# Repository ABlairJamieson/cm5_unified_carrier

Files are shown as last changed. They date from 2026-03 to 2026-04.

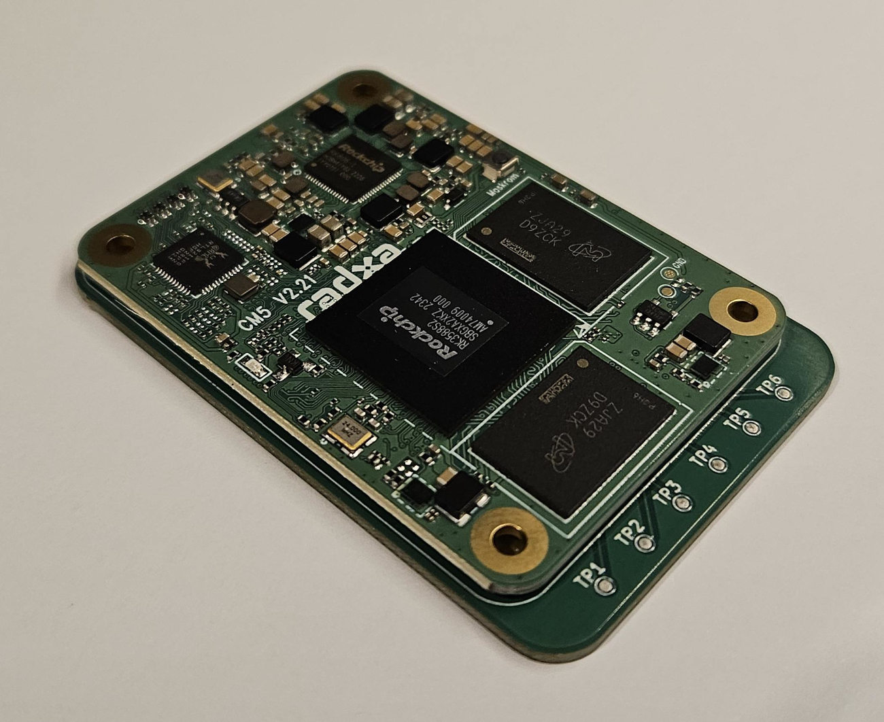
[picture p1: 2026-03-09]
include/radxa-cm5-kicad-main/radxa-cm5-kicad-main/screenshots/pcb-photo.jpg

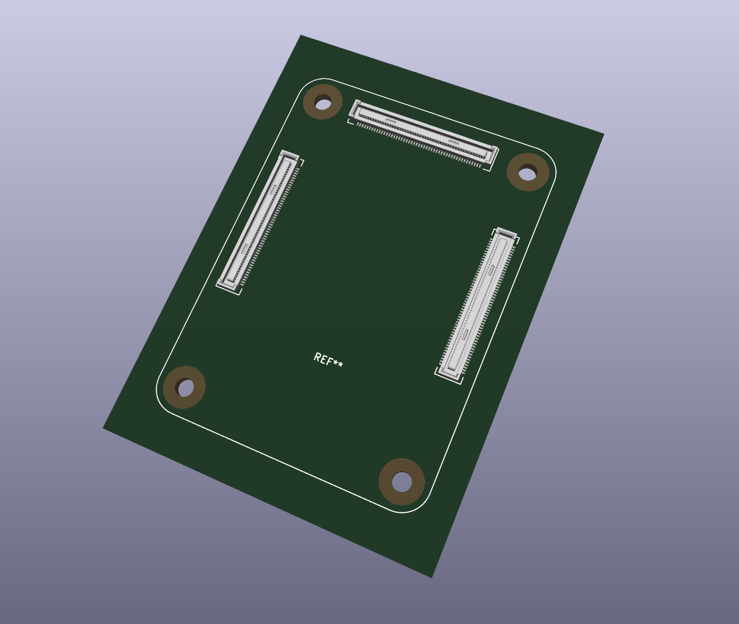
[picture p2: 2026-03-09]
include/radxa-cm5-kicad-main/radxa-cm5-kicad-main/screenshots/3d-model.png

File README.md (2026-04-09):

# CM5 Unified Carrier

Carrier board for Radxa CM5 used in the Hyper-K camera system.

Features:
- 48V input
- PoE option
- USB3 camera interface
- Ethernet
- Uses drop in DC/DC modules for 48V->12V (ext power mode)
- Uses drop in DC/DC module for 12V->8V (IWCD camera)
- Uses drop in DC/DC module for 12V->5V (both cameras)



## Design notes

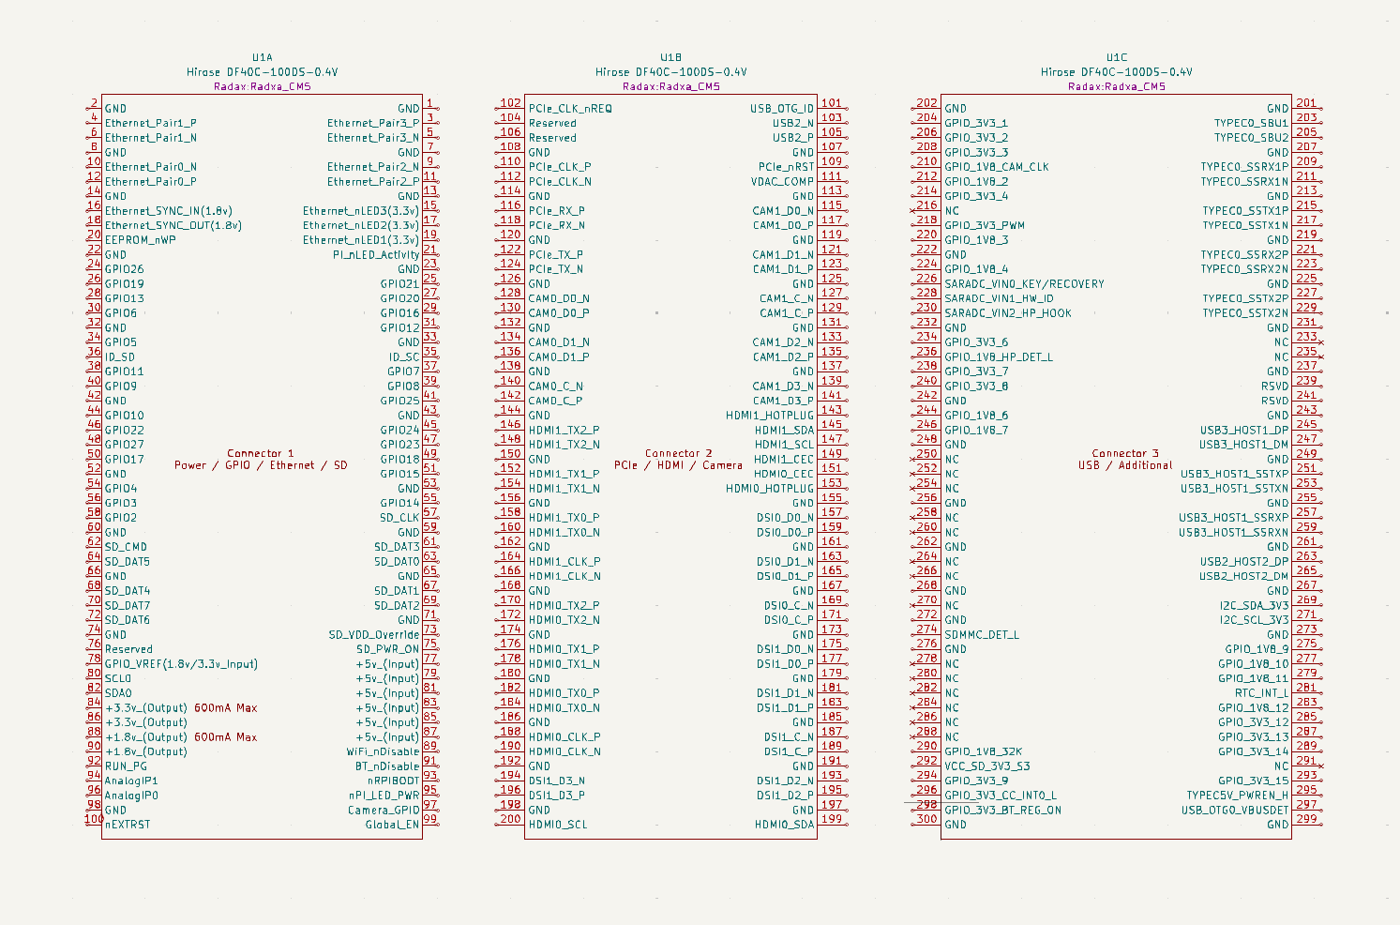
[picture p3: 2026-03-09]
include/radxa-cm5-kicad-main/radxa-cm5-kicad-main/screenshots/schematic.png

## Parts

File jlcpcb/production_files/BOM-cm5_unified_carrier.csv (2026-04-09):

Comment | Designator | Footprint | LCSC | Quantity
0Ohm | R101,R102 | R_1206_3216Metric_Pad1.30x1.75mm_HandSolder | C17888 | 2
10uF | C101,C102,C103,C406 | C_1206_3216Metric_Pad1.33x1.80mm_HandSolder | C89632 | 4
1uF | C302 | C_0805_2012Metric_Pad1.18x1.45mm_HandSolder | C28323 | 1
22uF | C404 | C_1206_3216Metric_Pad1.33x1.80mm_HandSolder | C12891 | 1
484050003 | J103 | CONN_484050003_MOL | C6058327 | 1
SMAJ58A | D101,D201 | D_SMA | C151246 | 2
PJ-102AH | J102 | CUI_PJ-102AH |  | 1
7499511002A | J201 | T_Wurth_WE-RJ45LAN_7499511002A |  | 1
436500403 | J101 | MOLEX_436500403 |  | 1
AG5712-LPB | U201 | MODULE_AG5712-LPB |  | 1
GND | TP403 | TestPoint_Pad_D1.5mm |  | 1
V8 | TP401 | TestPoint_Pad_D1.5mm |  | 1
GND | TP302 | TestPoint_Pad_D1.5mm |  | 1
V12 | TP301 | TestPoint_Pad_D1.5mm |  | 1
1.34kOhm | R402 | R_0805_2012Metric_Pad1.20x1.40mm_HandSolder |  | 1
2.49kOhm | R401 | R_0805_2012Metric_Pad1.20x1.40mm_HandSolder |  | 1
DNP | R301 | R_0805_2012Metric_Pad1.20x1.40mm_HandSolder |  | 1
I6A24014A033V-002-R | PS401 | CONV_I6A24014A033V-002-R |  | 1
ULS-12_5-D48N-C | PS301 | CONV_ULS-12_5-D48N-C |  | 1
OKL2-T_6-W12N-C | MD401 | MURATA_OKL2-T-6-W12N-C_0 |  | 1
PJ-102AH | J401 | CUI_PJ-102AH |  | 1
FerriteBead | FB101 | FB_Wurth_WE-CBF-1206_W5.2 |  | 1
10uF | C405 | C_1206_3216Metric_Pad1.33x1.80mm_HandSolder |  | 1
22uF | C403 | C_1206_3216Metric_Pad1.33x1.80mm_HandSolder |  | 1
0.1 uF | C402 | C_0805_2012Metric_Pad1.18x1.45mm_HandSolder |  | 1
100 uF | C401 | CP_Elec_6.3x5.8 |  | 1
10uF | C301 | CP_Elec_6.3x5.4 |  | 1
470uF | C204 | CP_Elec_8x6.5 |  | 1
10uF | C203 | C_1206_3216Metric_Pad1.33x1.80mm_HandSolder |  | 1
1uF | C202 | C_0805_2012Metric_Pad1.18x1.45mm_HandSolder |  | 1
10nF | C201 | C_1206_3216Metric_Pad1.33x1.80mm_HandSolder |  | 1
Hirose DF40C-100DS-0.4V | J501 | Radxa_CM5 |  | 1
484050003 | J104 | CONN_484050003_MOL |  | 1
1050170001 | J105 | USB_Micro_B_Female_1050170001 |  | 1
Conn_01x02_Pin | J601 | PinHeader_1x02_P2.54mm_Vertical |  | 1
SW_Push | SW501 | SW_SPST_EVQP7A |  | 1
V5 | TP402 | TestPoint_Pad_D1.5mm |  | 1
PoE+ | TP202 | TestPoint_Pad_D1.5mm |  | 1
PoE- | TP201 | TestPoint_Pad_D1.5mm |  | 1
ABS10 | BR201 | SOT200P640X160-4N |  | 1
ABS10 | BR202 | SOT200P640X160-4N |  | 1

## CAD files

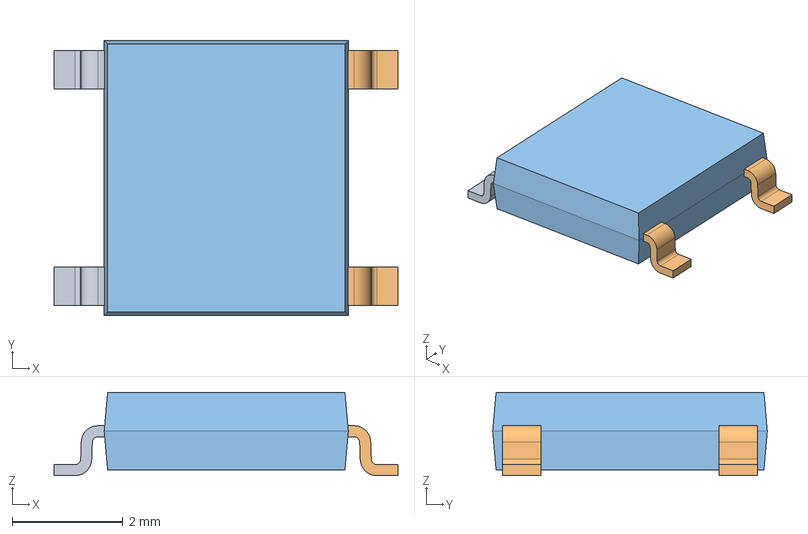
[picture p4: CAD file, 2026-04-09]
include/ABS10/ABS10.step
6.20 x 4.95 x 1.50 mm

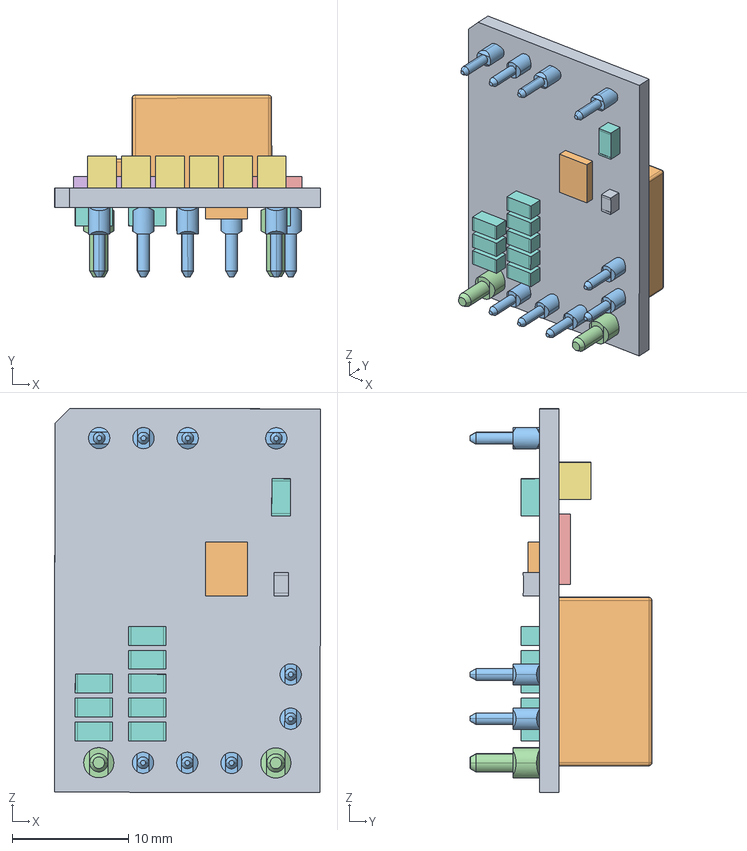
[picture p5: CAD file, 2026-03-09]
include/I6A24014A033V-002-R/I6A24014A033V-002-R.step
22.9 x 15.7 x 33.0 mm
I6A_PCB
I6A_OUTPUT_INDUCTOR
ZP00166_01- x 9
ZP00167_01- x 2
I6A_LOW_SIDE_FET
I6A_HIGH_SIDE_FET x 2
1210_CAP_COLOR x 6
1206_CAP_COLOR x 9
0805_CAP
I6A_CONTROL_IC2

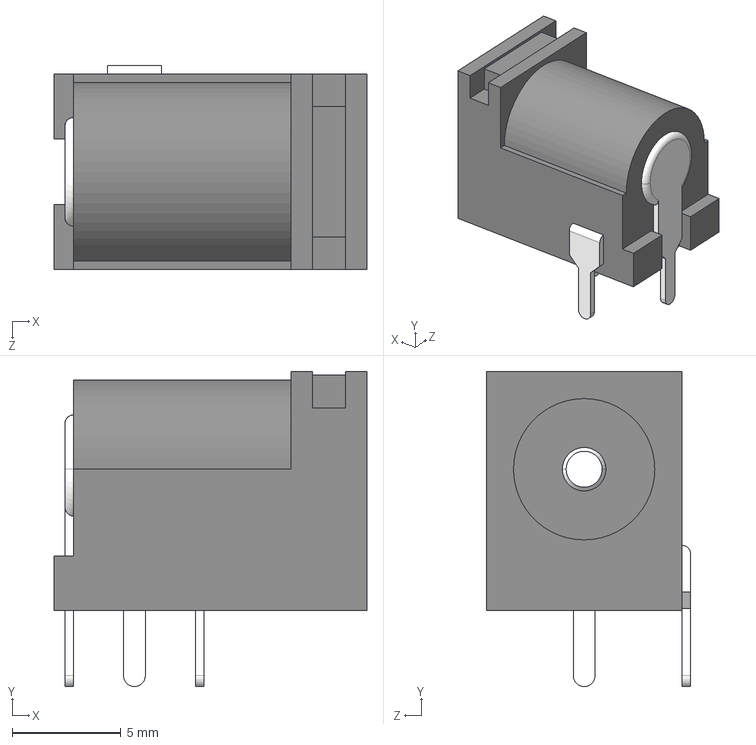
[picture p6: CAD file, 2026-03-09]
include/PJ-102AH/PJ-102AH.step
14.4 x 14.5 x 9.40 mm

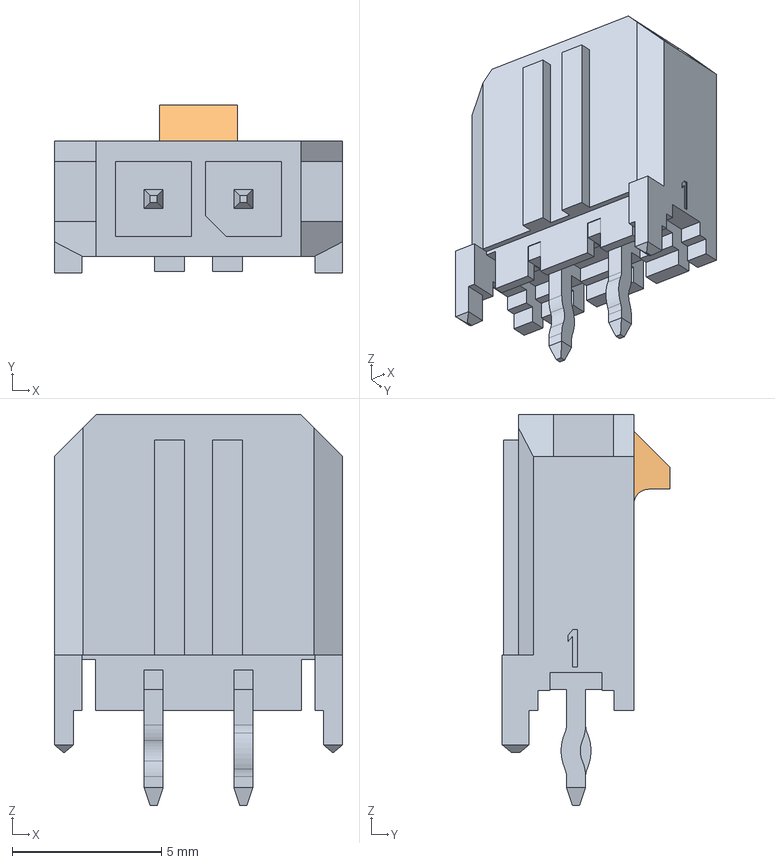
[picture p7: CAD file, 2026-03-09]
include/436500215/436500215.step
9.65 x 5.61 x 13.1 mm

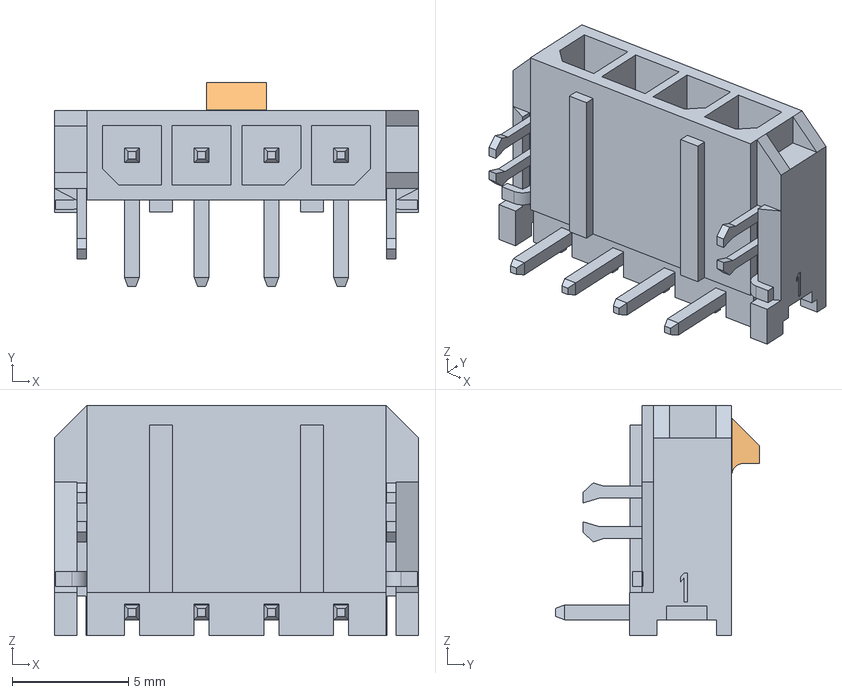
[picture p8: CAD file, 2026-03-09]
include/436500403/436500403.step
15.7 x 8.79 x 9.90 mm

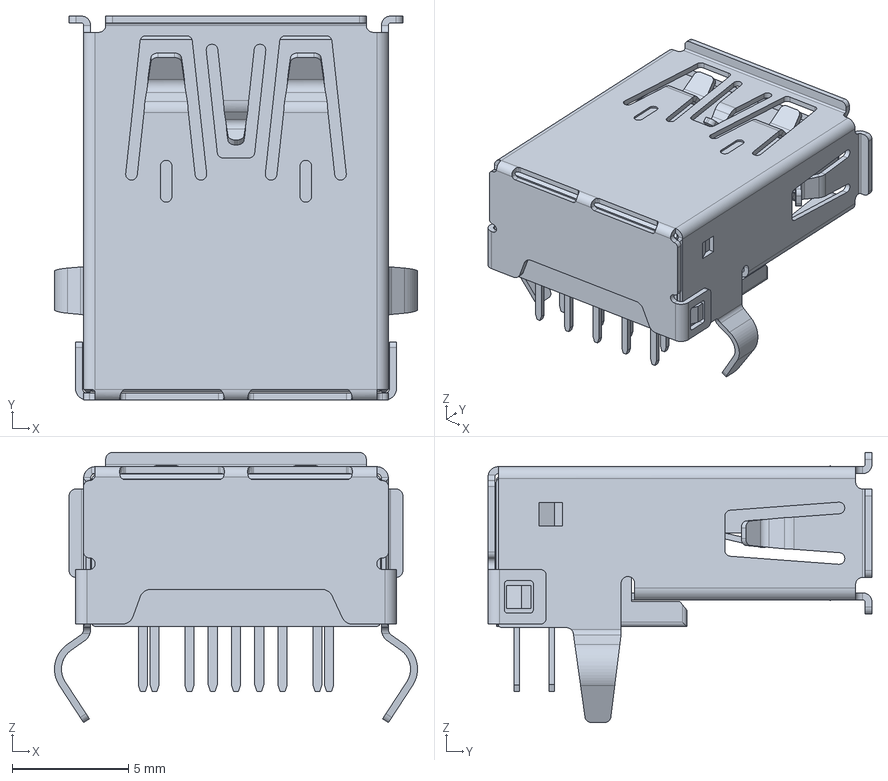
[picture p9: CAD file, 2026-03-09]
include/484050003/484050003.stp
15.6 x 16.5 x 11.6 mm

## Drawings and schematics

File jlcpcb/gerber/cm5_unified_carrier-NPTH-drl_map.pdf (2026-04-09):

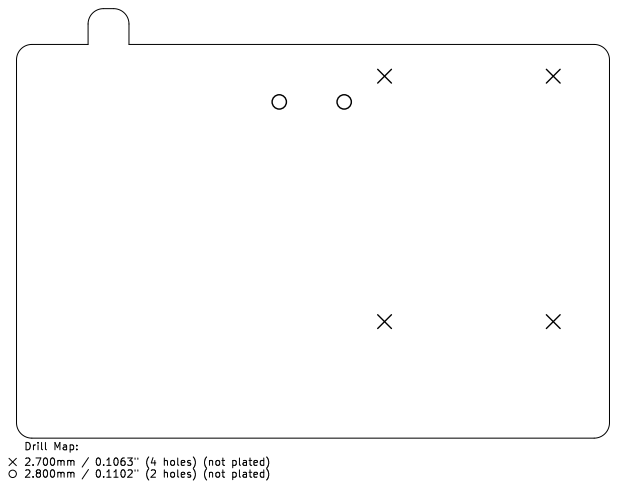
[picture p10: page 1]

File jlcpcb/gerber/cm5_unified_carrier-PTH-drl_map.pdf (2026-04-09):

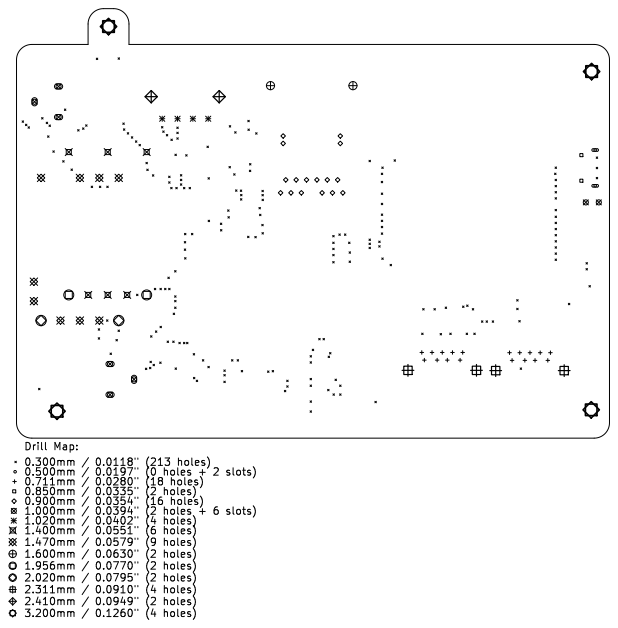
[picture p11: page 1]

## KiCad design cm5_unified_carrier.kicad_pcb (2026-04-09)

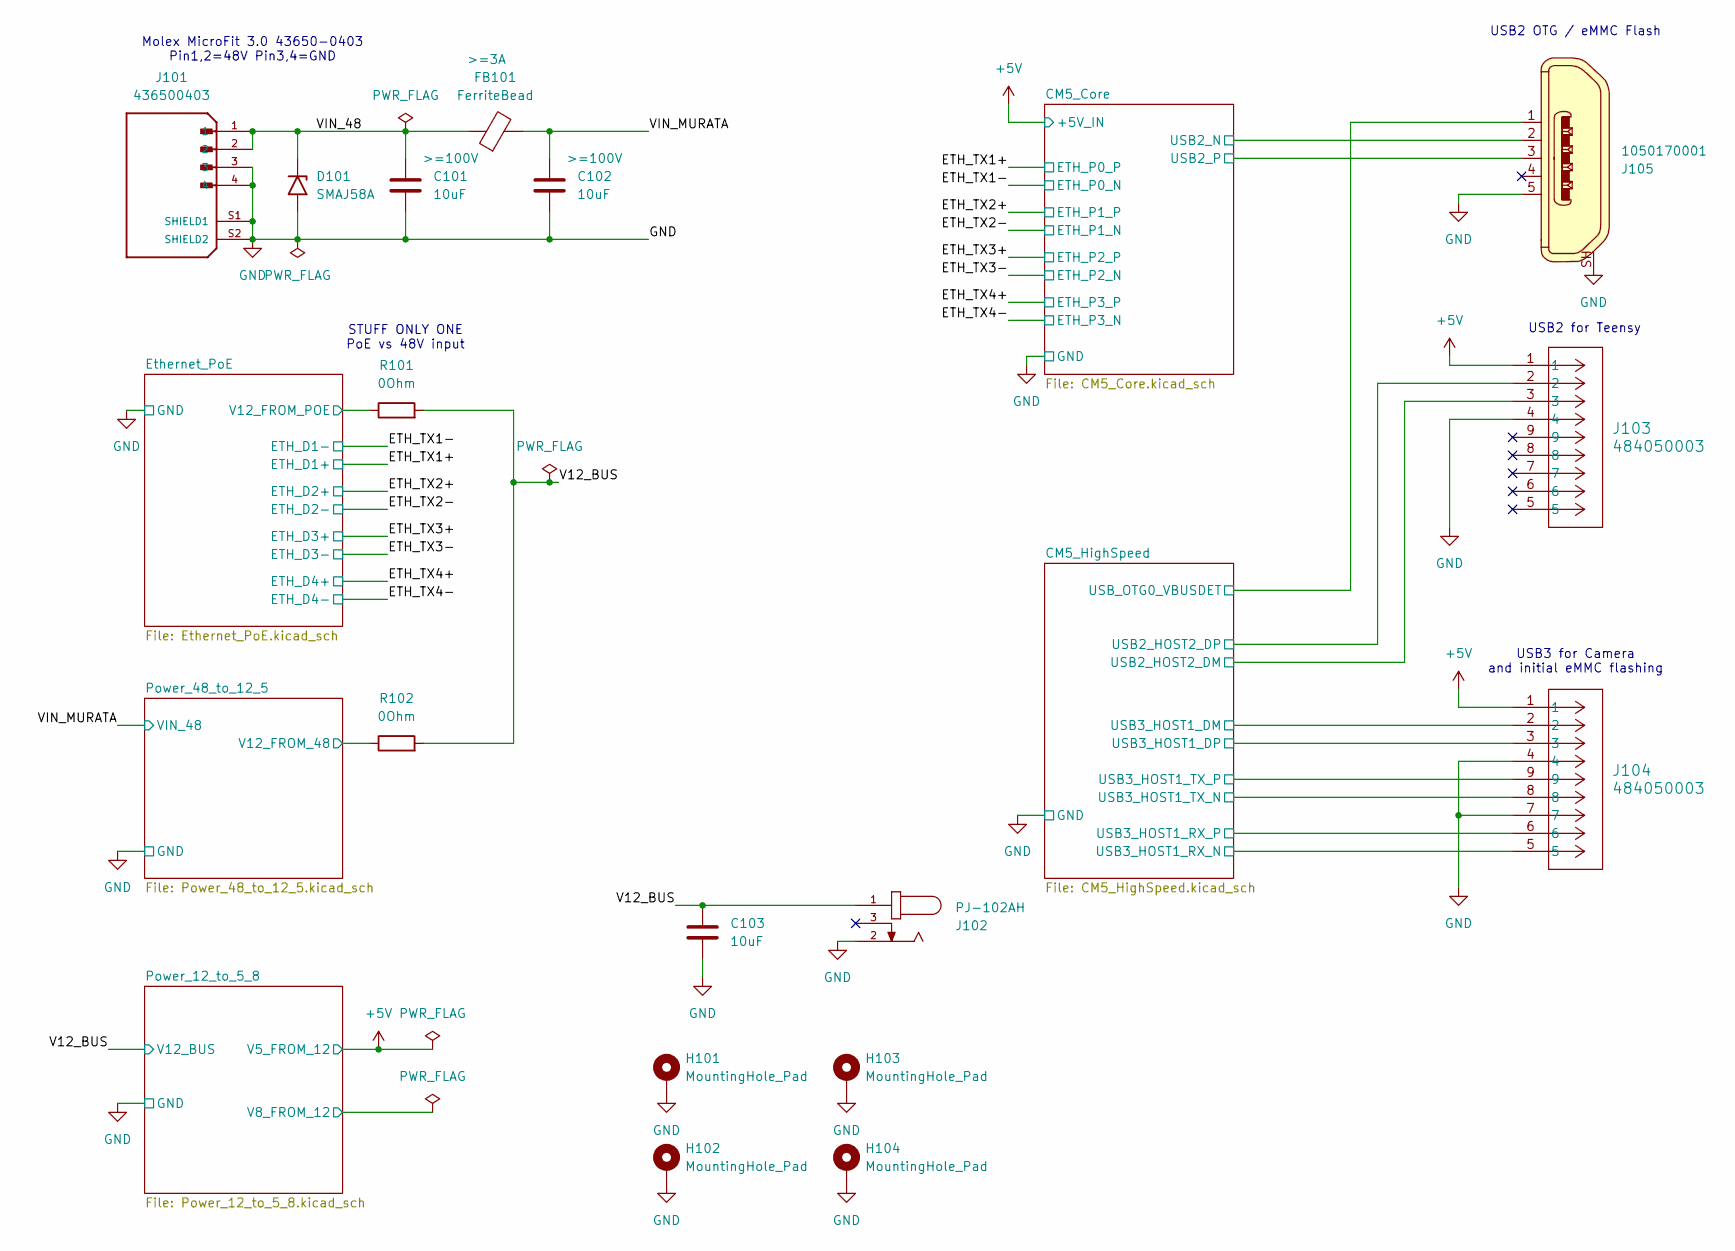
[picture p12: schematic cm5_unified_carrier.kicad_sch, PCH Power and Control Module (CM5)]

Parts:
C101, C102, C103: 10uF; C_1206_3216Metric_Pad1.33x1.80mm_HandSolder
D101: SMAJ58A; D_SMA
FB101: FerriteBead; FB_Wurth_WE-CBF-1206_W5.2
H101, H102, H103, H104: MountingHole_Pad; MountingHole_3.2mm_M3_DIN965_Pad
J101: 436500403; MOLEX_436500403; PARTREV F3
J102: PJ-102AH; CUI_PJ-102AH
J103, J104: 484050003; CONN_484050003_MOL
J105: 1050170001; USB_Micro_B_Female_1050170001; MPN 1050170001; Digi-Key_PN WM1399CT-ND
R101, R102: 0Ohm; R_1206_3216Metric_Pad1.30x1.75mm_HandSolder

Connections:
+5V: J103.1, J104.1; also elsewhere on the board
/CM5_Core/USB2_N: J105.2; also elsewhere on the board
/CM5_Core/USB2_P: J105.3; also elsewhere on the board
/CM5_HighSpeed/USB2_HOST2_DM: J103.3; also elsewhere on the board
/CM5_HighSpeed/USB2_HOST2_DP: J103.2; also elsewhere on the board
/CM5_HighSpeed/USB3_HOST1_DM: J104.2; also elsewhere on the board
/CM5_HighSpeed/USB3_HOST1_DP: J104.3; also elsewhere on the board
/CM5_HighSpeed/USB3_HOST1_SSRXN: J104.5; also elsewhere on the board
/CM5_HighSpeed/USB3_HOST1_SSRXP: J104.6; also elsewhere on the board
/CM5_HighSpeed/USB3_HOST1_SSTXN: J104.8; also elsewhere on the board
/CM5_HighSpeed/USB3_HOST1_SSTXP: J104.9; also elsewhere on the board
/CM5_HighSpeed/USB_OTG0_VBUSDET: J105.1; also elsewhere on the board
/Ethernet_PoE/V12_FROM_POE: R101.1; also elsewhere on the board
/Power_48_to_12_5/V12_FROM_48: R102.1; also elsewhere on the board
/V12_BUS: C103.1, J102.1, R101.2, R102.2; also elsewhere on the board
/VIN_48: C101.1, D101.1 (A1), FB101.1, J101.1, J101.2
/VIN_MURATA: C102.1, FB101.2; also elsewhere on the board
GND: C101.2, C102.2, C103.2, D101.2 (A2), H101.1, H102.1, H103.1, H104.1, J101.3, J101.4, J101.S1 (SHIELD1), J101.S2 (SHIELD2), J102.2, J103.4, J104.4, J104.7, J105.5, J105.SH; also elsewhere on the board

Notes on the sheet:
STUFF ONLY ONE PoE vs 48V input
USB2 for Teensy
USB2 OTG / eMMC Flash
USB3 for Camera and initial eMMC flashing
Molex MicroFit 3.0 43650-0403 Pin1,2=48V Pin3,4=GND

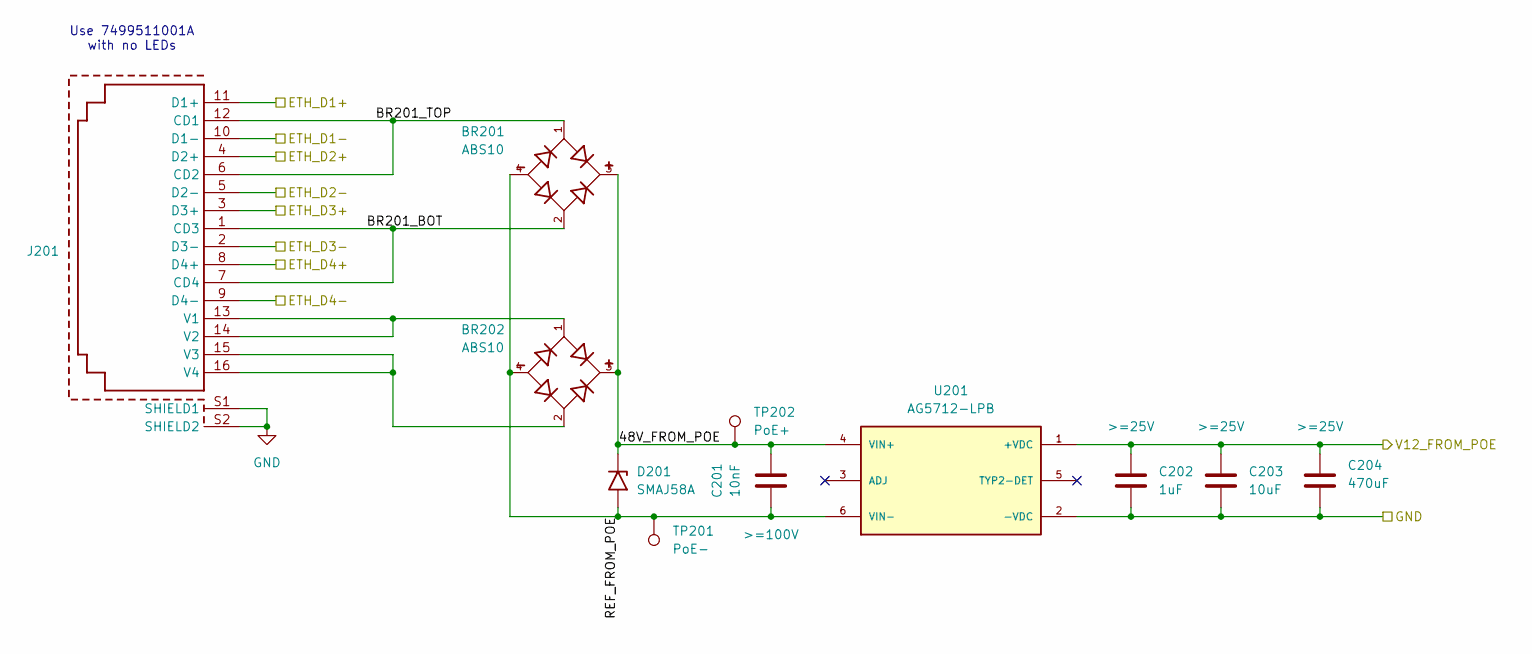
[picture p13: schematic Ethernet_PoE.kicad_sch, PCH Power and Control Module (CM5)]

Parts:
BR201, BR202: ABS10; SOT200P640X160-4N; PART_REV 4
C201: 10nF; C_1206_3216Metric_Pad1.33x1.80mm_HandSolder
C202: 1uF; C_0805_2012Metric_Pad1.18x1.45mm_HandSolder
C203: 10uF; C_1206_3216Metric_Pad1.33x1.80mm_HandSolder
C204: 470uF; CP_Elec_8x6.5
D201: SMAJ58A; D_SMA
J201: 7499511002A; T_Wurth_WE-RJ45LAN_7499511002A; Part Number 7499511002A
TP201: PoE-; TestPoint_Pad_D1.5mm
TP202: PoE+; TestPoint_Pad_D1.5mm
U201: AG5712-LPB; MODULE_AG5712-LPB; PARTREV V1.1

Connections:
/ETH_TX1+: J201.11 (D1+); also elsewhere on the board
/ETH_TX1-: J201.10 (D1-); also elsewhere on the board
/ETH_TX2+: J201.4 (D2+); also elsewhere on the board
/ETH_TX2-: J201.5 (D2-); also elsewhere on the board
/ETH_TX3+: J201.3 (D3+); also elsewhere on the board
/ETH_TX3-: J201.2 (D3-); also elsewhere on the board
/ETH_TX4+: J201.8 (D4+); also elsewhere on the board
/ETH_TX4-: J201.9 (D4-); also elsewhere on the board
/Ethernet_PoE/48V_FROM_POE: BR201.3, BR202.3, C201.2, D201.1 (A1), TP202.1, U201.4 (VIN+)
/Ethernet_PoE/BR201_BOT: BR201.2, J201.1 (CD3), J201.7 (CD4)
/Ethernet_PoE/BR201_TOP: BR201.1, J201.6 (CD2), J201.12 (CD1)
/Ethernet_PoE/REF_FROM_POE: BR201.4, BR202.4, C201.1, D201.2 (A2), TP201.1, U201.6 (VIN-)
/Ethernet_PoE/V12_FROM_POE: C202.1, C203.1, C204.1, U201.1 (+VDC); also elsewhere on the board
GND: C202.2, C203.2, C204.2, J201.S1 (SHIELD1), J201.S2 (SHIELD2), U201.2 (-VDC); also elsewhere on the board
unnamed: BR202.1, J201.13 (V1), J201.14 (V2)
unnamed: BR202.2, J201.15 (V3), J201.16 (V4)

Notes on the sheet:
Use 7499511001A with no LEDs

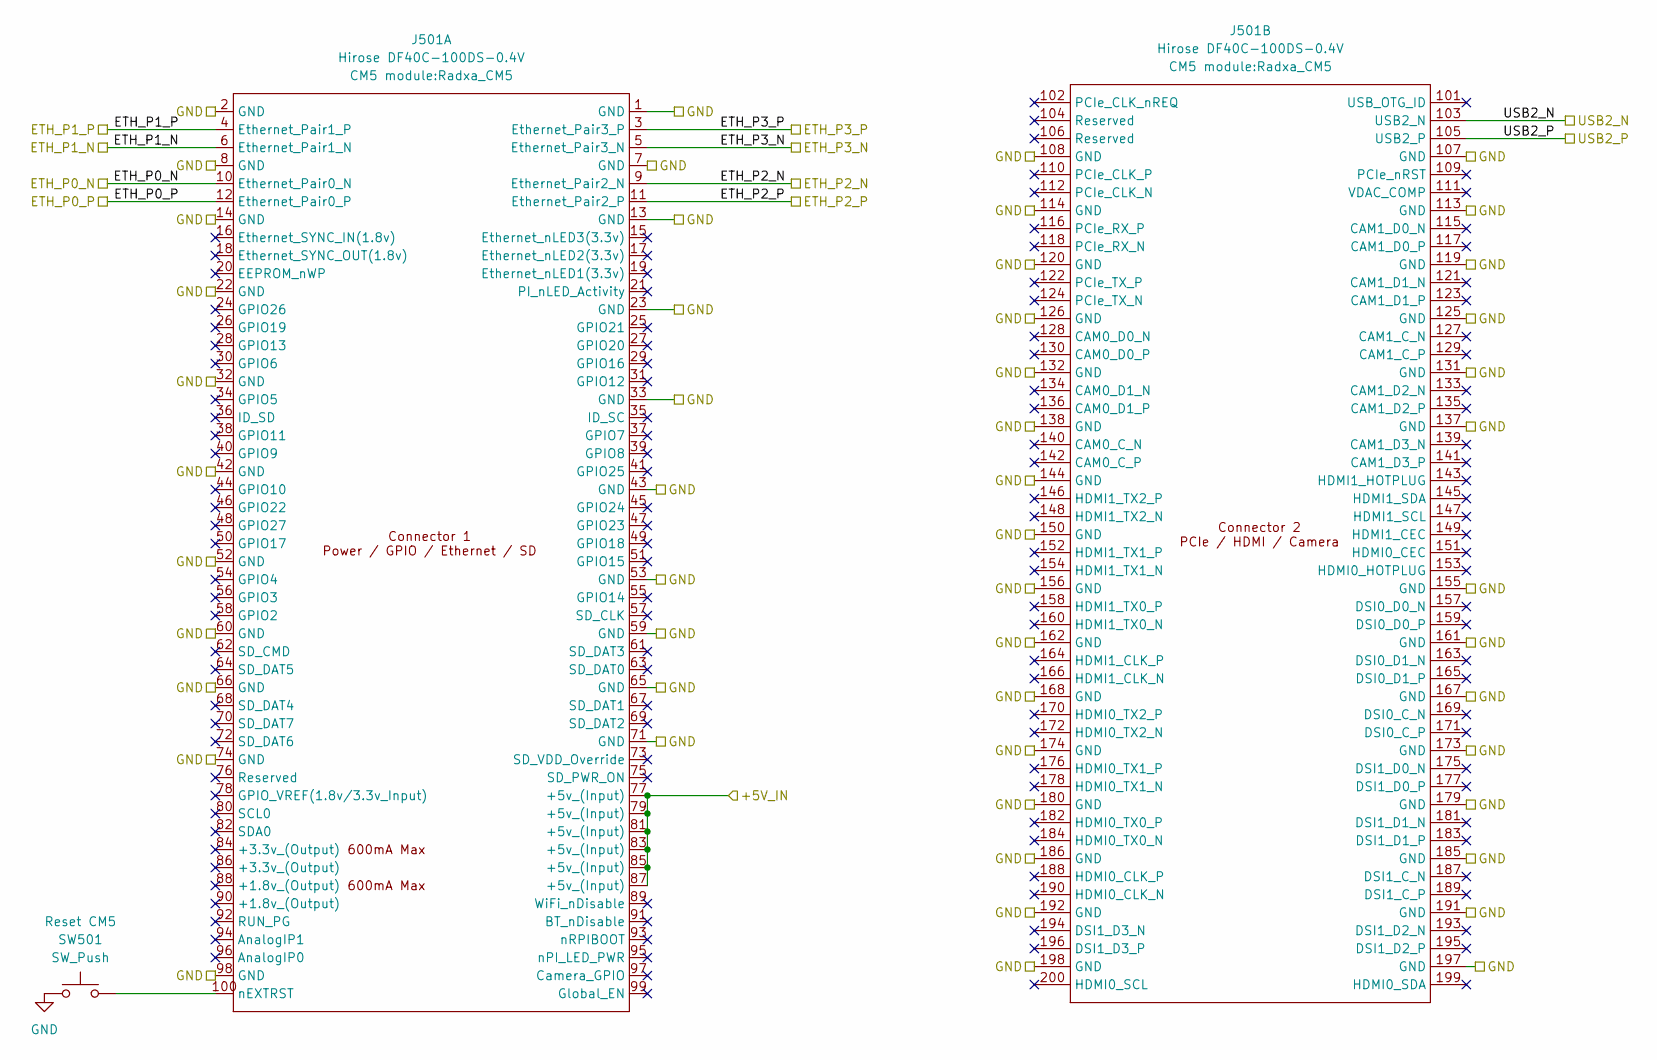
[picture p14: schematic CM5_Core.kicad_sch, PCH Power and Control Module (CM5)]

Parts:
J501: Hirose DF40C-100DS-0.4V; Radxa_CM5
SW501: SW_Push; SW_SPST_EVQP7A

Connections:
+5V: J501.77 (+5v_(Input)), J501.79 (+5v_(Input)), J501.81 (+5v_(Input)), J501.83 (+5v_(Input)), J501.85 (+5v_(Input)), J501.87 (+5v_(Input)); also elsewhere on the board
/CM5_Core/USB2_N: J501.103 (USB2_N); also elsewhere on the board
/CM5_Core/USB2_P: J501.105 (USB2_P); also elsewhere on the board
/ETH_TX1+: J501.12 (Ethernet_Pair0_P); also elsewhere on the board
/ETH_TX1-: J501.10 (Ethernet_Pair0_N); also elsewhere on the board
/ETH_TX2+: J501.4 (Ethernet_Pair1_P); also elsewhere on the board
/ETH_TX2-: J501.6 (Ethernet_Pair1_N); also elsewhere on the board
/ETH_TX3+: J501.11 (Ethernet_Pair2_P); also elsewhere on the board
/ETH_TX3-: J501.9 (Ethernet_Pair2_N); also elsewhere on the board
/ETH_TX4+: J501.3 (Ethernet_Pair3_P); also elsewhere on the board
/ETH_TX4-: J501.5 (Ethernet_Pair3_N); also elsewhere on the board
GND: J501.1 (GND), J501.2 (GND), J501.7 (GND), J501.8 (GND), J501.13 (GND), J501.14 (GND), J501.22 (GND), J501.23 (GND), J501.32 (GND), J501.33 (GND), J501.42 (GND), J501.43 (GND), J501.52 (GND), J501.53 (GND), J501.59 (GND), J501.60 (GND), J501.65 (GND), J501.66 (GND), J501.71 (GND), J501.74 (GND), J501.98 (GND), J501.107 (GND), J501.108 (GND), J501.113 (GND), J501.114 (GND), J501.119 (GND), J501.120 (GND), J501.125 (GND), J501.126 (GND), J501.131 (GND), J501.132 (GND), J501.137 (GND), J501.138 (GND), J501.144 (GND), J501.150 (GND), J501.155 (GND), J501.156 (GND), J501.161 (GND), J501.162 (GND), J501.167 (GND), J501.168 (GND), J501.173 (GND), J501.174 (GND), J501.179 (GND), J501.180 (GND), J501.185 (GND), J501.186 (GND), J501.191 (GND), J501.192 (GND), J501.197 (GND), J501.198 (GND), SW501.1; also elsewhere on the board
unnamed: J501.100 (nEXTRST), SW501.2

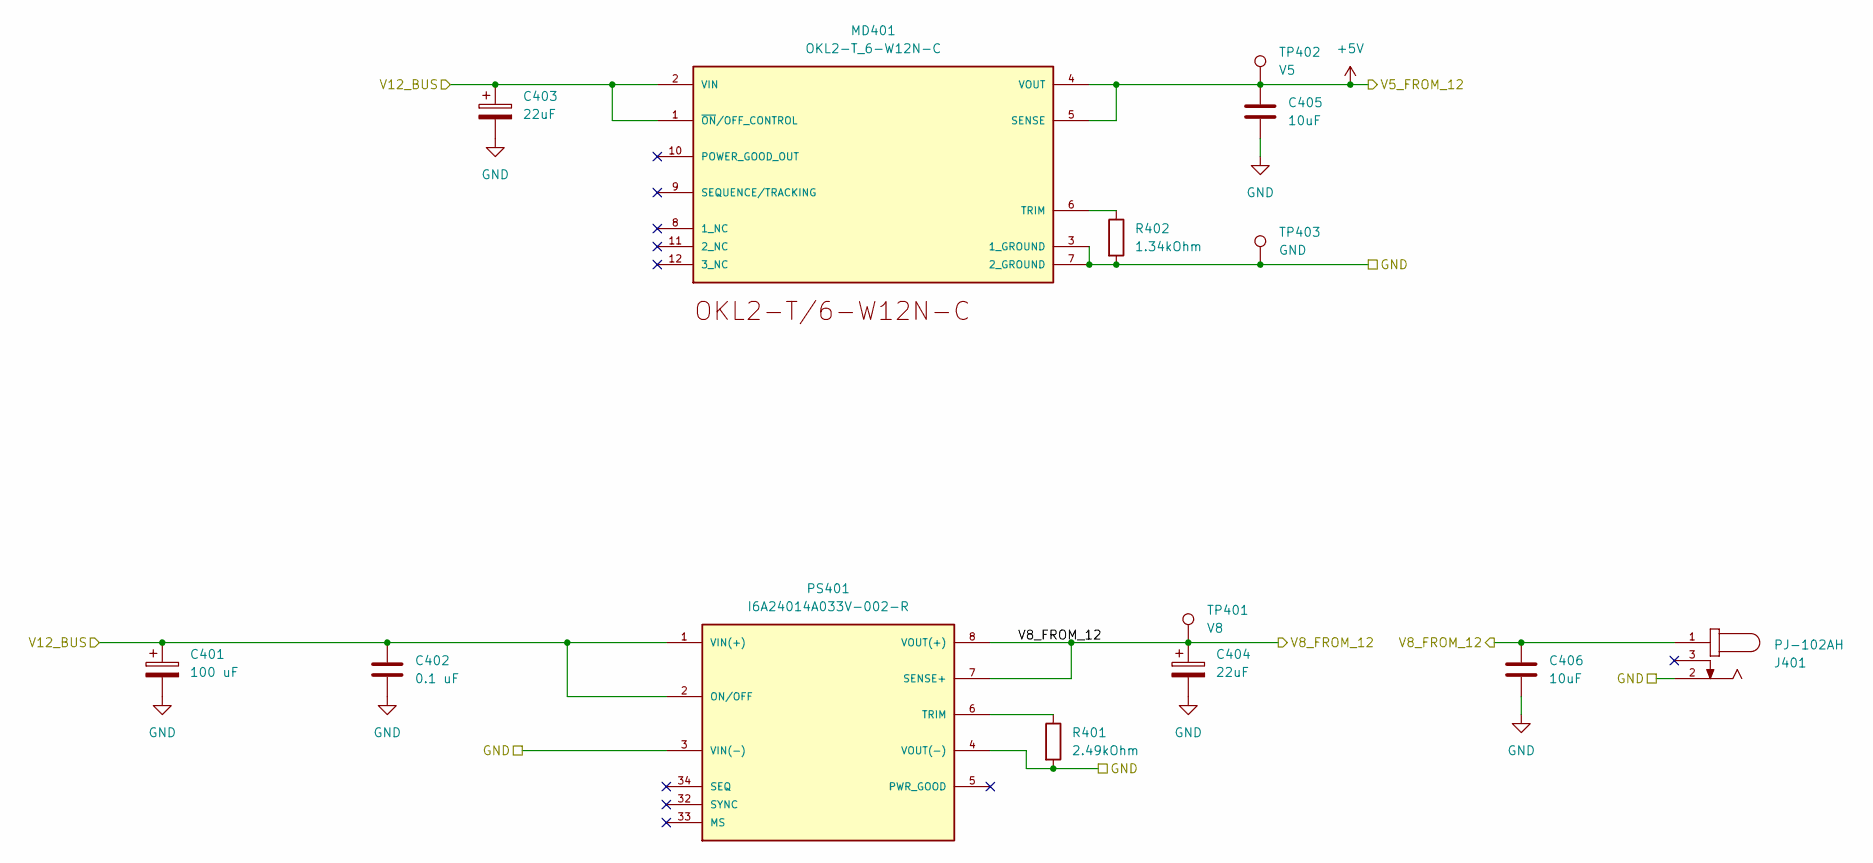
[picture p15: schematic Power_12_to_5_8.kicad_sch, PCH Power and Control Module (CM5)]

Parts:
C401: 100 uF; CP_Elec_6.3x5.8
C402: 0.1 uF; C_0805_2012Metric_Pad1.18x1.45mm_HandSolder
C403, C404: 22uF; C_1206_3216Metric_Pad1.33x1.80mm_HandSolder
C405, C406: 10uF; C_1206_3216Metric_Pad1.33x1.80mm_HandSolder
J401: PJ-102AH; CUI_PJ-102AH
MD401: OKL2-T_6-W12N-C; MURATA_OKL2-T-6-W12N-C_0; MOUSER_PART_NUMBER 580-OKL2-T/6-W12N-C; MOUSER_DESCRIPTION Non-Isolated DC/DC Converters 12Vin .59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
PS401: I6A24014A033V-002-R; CONV_I6A24014A033V-002-R; PARTREV A2; DigiKey_Part_Number 285-2857-ND
R401: 2.49kOhm; R_0805_2012Metric_Pad1.20x1.40mm_HandSolder
R402: 1.34kOhm; R_0805_2012Metric_Pad1.20x1.40mm_HandSolder
TP401: V8; TestPoint_Pad_D1.5mm
TP402: V5; TestPoint_Pad_D1.5mm
TP403: GND; TestPoint_Pad_D1.5mm

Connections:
+5V: C405.1, MD401.4 (VOUT), MD401.5 (SENSE), TP402.1; also elsewhere on the board
/Power_12_to_5_8/V8_FROM_12: C404.1, C406.1, J401.1, PS401.7 (SENSE+), PS401.8 (VOUT(+)), TP401.1
/V12_BUS: C401.1, C402.1, C403.1, MD401.1 (~ON/OFF_CONTROL), MD401.2 (VIN), PS401.1 (VIN(+)), PS401.2 (ON/OFF); also elsewhere on the board
GND: C401.2, C402.2, C403.2, C404.2, C405.2, C406.2, J401.2, MD401.3 (1_GROUND), MD401.7 (2_GROUND), PS401.3 (VIN(-)), PS401.4 (VOUT(-)), R401.2, R402.2, TP403.1; also elsewhere on the board
unnamed: MD401.6 (TRIM), R402.1
unnamed: PS401.6 (TRIM), R401.1

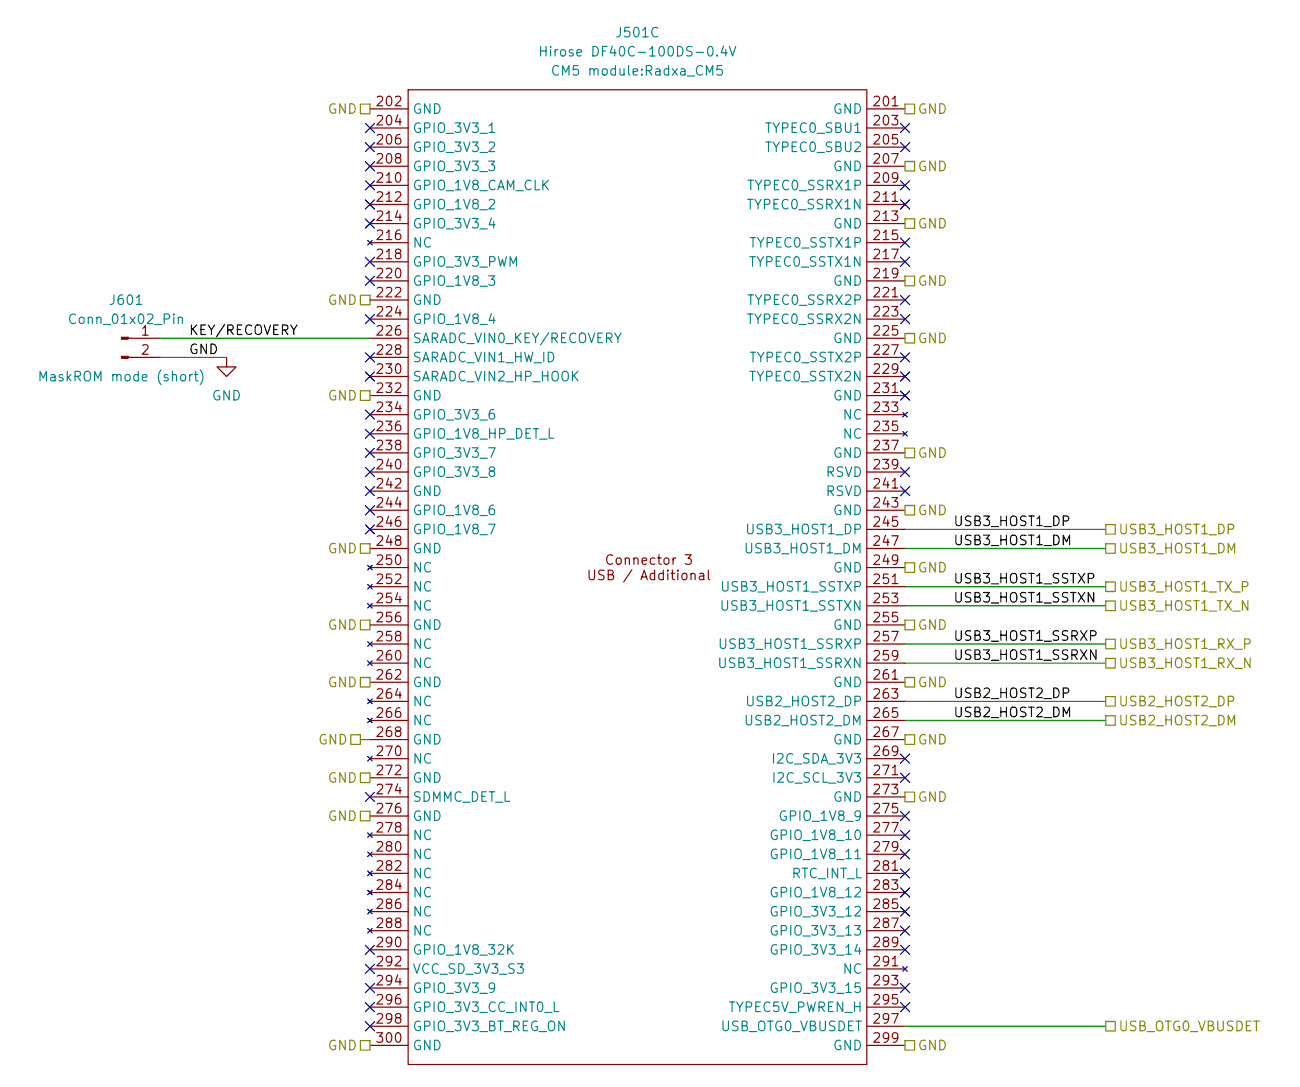
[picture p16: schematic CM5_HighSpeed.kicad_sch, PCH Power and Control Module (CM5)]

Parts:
J501: Hirose DF40C-100DS-0.4V; Radxa_CM5
J601: Conn_01x02_Pin; PinHeader_1x02_P2.54mm_Vertical

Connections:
/CM5_HighSpeed/KEY/RECOVERY: J501.226 (SARADC_VIN0_KEY/RECOVERY), J601.1
/CM5_HighSpeed/USB2_HOST2_DM: J501.265 (USB2_HOST2_DM); also elsewhere on the board
/CM5_HighSpeed/USB2_HOST2_DP: J501.263 (USB2_HOST2_DP); also elsewhere on the board
/CM5_HighSpeed/USB3_HOST1_DM: J501.247 (USB3_HOST1_DM); also elsewhere on the board
/CM5_HighSpeed/USB3_HOST1_DP: J501.245 (USB3_HOST1_DP); also elsewhere on the board
/CM5_HighSpeed/USB3_HOST1_SSRXN: J501.259 (USB3_HOST1_SSRXN); also elsewhere on the board
/CM5_HighSpeed/USB3_HOST1_SSRXP: J501.257 (USB3_HOST1_SSRXP); also elsewhere on the board
/CM5_HighSpeed/USB3_HOST1_SSTXN: J501.253 (USB3_HOST1_SSTXN); also elsewhere on the board
/CM5_HighSpeed/USB3_HOST1_SSTXP: J501.251 (USB3_HOST1_SSTXP); also elsewhere on the board
/CM5_HighSpeed/USB_OTG0_VBUSDET: J501.297 (USB_OTG0_VBUSDET); also elsewhere on the board
GND: J501.201 (GND), J501.202 (GND), J501.207 (GND), J501.213 (GND), J501.219 (GND), J501.222 (GND), J501.225 (GND), J501.232 (GND), J501.237 (GND), J501.243 (GND), J501.248 (GND), J501.249 (GND), J501.255 (GND), J501.256 (GND), J501.261 (GND), J501.262 (GND), J501.267 (GND), J501.268 (GND), J501.272 (GND), J501.273 (GND), J501.276 (GND), J501.299 (GND), J501.300 (GND), J601.2; also elsewhere on the board

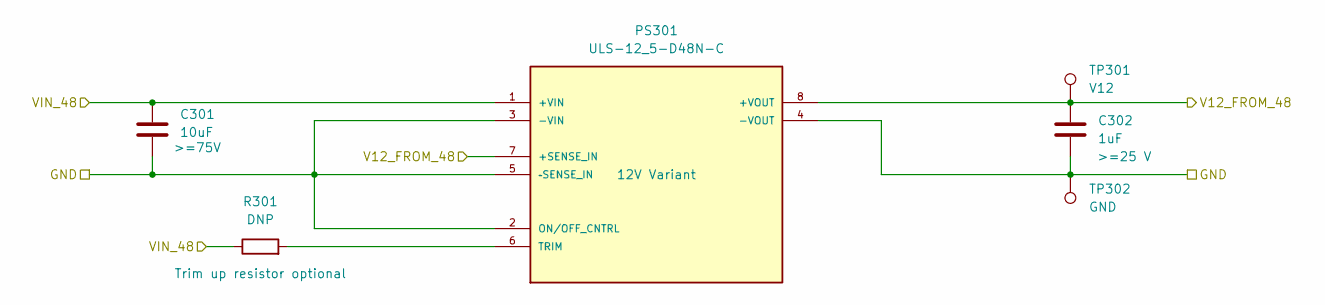
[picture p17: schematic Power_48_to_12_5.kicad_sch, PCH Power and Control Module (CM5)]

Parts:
C301: 10uF; CP_Elec_6.3x5.4
C302: 1uF; C_0805_2012Metric_Pad1.18x1.45mm_HandSolder
PS301: ULS-12_5-D48N-C; CONV_ULS-12_5-D48N-C
R301: DNP; R_0805_2012Metric_Pad1.20x1.40mm_HandSolder
TP301: V12; TestPoint_Pad_D1.5mm
TP302: GND; TestPoint_Pad_D1.5mm

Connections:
/Power_48_to_12_5/V12_FROM_48: C302.1, PS301.7 (+SENSE_IN), PS301.8 (+VOUT), TP301.1; also elsewhere on the board
/VIN_MURATA: C301.1, PS301.1 (+VIN), R301.1; also elsewhere on the board
GND: C301.2, C302.2, PS301.2 (ON/OFF_CNTRL), PS301.3 (-VIN), PS301.4 (-VOUT), PS301.5 (–SENSE_IN), TP302.1; also elsewhere on the board
unnamed: PS301.6 (TRIM), R301.2

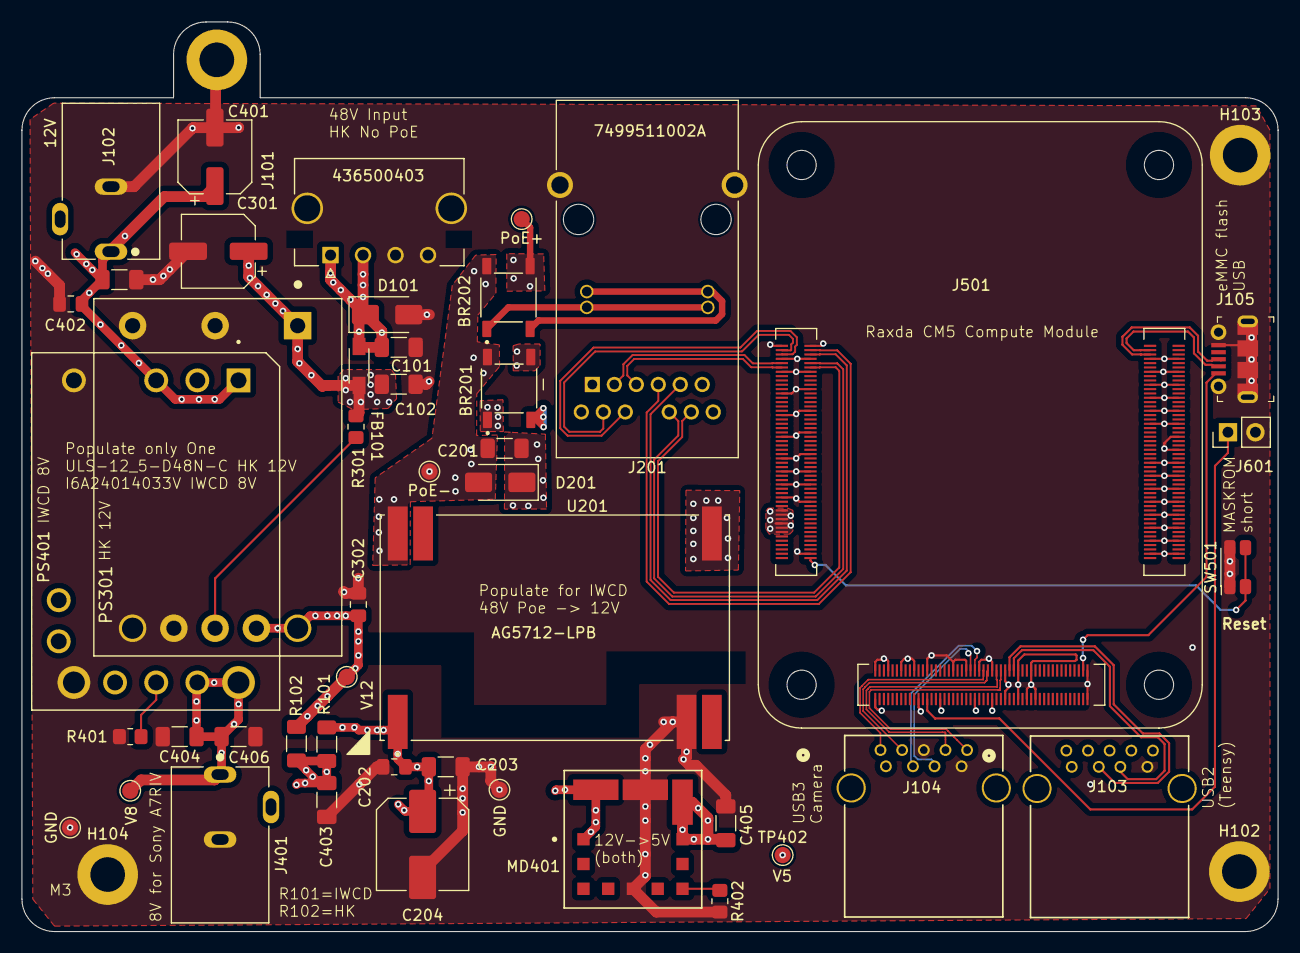
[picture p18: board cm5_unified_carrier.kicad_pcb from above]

Board: 4 copper layers, 116.0 x 84.0 mm, 50 parts (0 on the bottom side), 38 nets.

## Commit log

2026-03-09 Initial commit: CM5 carrier for camera control
    [436500215.step, 436500403.step, 484050003.stp, BOM-cm5_unified_carrier.csv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]
2026-03-09 Added another barrel jack for 12V output for ASI camera
    [BOM-cm5_unified_carrier.csv, CPL-cm5_unified_carrier.csv, cm5_unified_carrier-CuBottom.gbr, cm5_unified_carrier-CuIn1.gbr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]
2026-03-09 Added USB connector for flashing eMMC and related switches
    [CM5_Core.kicad_sch, CM5_HighSpeed.kicad_sch, cm5_unified_carrier.kicad_pcb, cm5_unified_carrier.kicad_sch]
2026-03-10 Reduced board size by allowing overlap of power modules where only one needs to be populated
    [cm5_unified_carrier.kicad_pcb]
2026-03-10 minor cleanup
    [BOM-cm5_unified_carrier.csv, CPL-cm5_unified_carrier.csv, cm5_unified_carrier-CuBottom.gbr, cm5_unified_carrier-CuIn1.gbr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]
2026-03-10 a few more minor updates
    [BOM-cm5_unified_carrier.csv, CPL-cm5_unified_carrier.csv, cm5_unified_carrier-CuBottom.gbr, cm5_unified_carrier-CuIn1.gbr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]
2026-04-09 Update to fix power connection mistakes in both IWCD and HK configurations. For IWCD added bridge rectifier diodes needed for PoE, for HK updated to look at correct ref voltage for the 12V generation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
    [ABS10.step, BOM-cm5_unified_carrier.csv, CPL-cm5_unified_carrier.csv, Ethernet_PoE.kicad_sch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]
